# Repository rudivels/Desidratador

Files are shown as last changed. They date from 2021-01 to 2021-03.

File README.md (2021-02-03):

# Desidratador automático de laboratório 

Projeto de desenvolver um desidratador de laboratorio a partir de um forno elétrico.

Desenvolvido por [Rudi van Els](http://fga.unb.br/rudi.van) inicio dezembro 2020.
 
`/Arduino/ESP12_Secador`

`/Arduino?ESP12_Secador/ESP12_Secador_modbus`

# 1. Apresentação 

Por que fazer este desidratador?
A demanda surgiu depois de observar o trabalho demorada de levantar curva de secagem de produtos em laboratório onde era necessária  fazer medidas da perda de massa durante horas ou dias. 

Um processo típico pode levar algumas horas, com a necessidade de registrar essa perda a intervalos regulares que variam de um a alguns dezenas de minutos. 

Como não tem desidratadores que fazem essas medidas automáticas, resolvi fazer um. Em vez de pegar um desidratador pronto, resolvemos adaptar um forne elétrico, pois os desidratadores comerciais no mercado não são muito apropriados para uso no laboratório por causa do seu tamanho. 

A escolha do usar um forne elétrico é por causa da grande variedades de modelos disponíveis no mercado a preços competitos. Entretanto, nada impede de pegar a tecnologia desenvolvido e adapta-lo a um desidratador comercial.  

Foi escolhido usar um modelo de forno de 36 litros mostrada na figura a seguir.
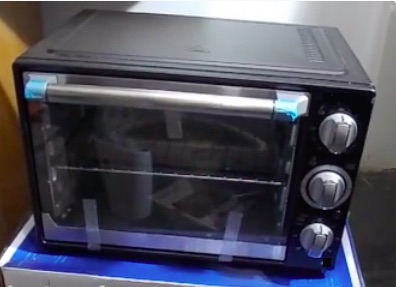
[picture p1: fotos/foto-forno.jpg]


O desidratador de laboratório deve ser capaz de:
 
- Medir a massa da amostra em tempo real durante o processo de desidratação;
- Medir dados de temperatura e umidade relativo do ar no ambiente e no desidratador;
- Armazenar estes dados no próprio equipamento;
- Controlar a temperatura dentro do desidratador;
- Controlar a vazão da entrada de ar no desidratador;
- Permitir o acesso aos dados por meio da internet;

A figura a seguir mostra a proposta do diagrama de bloco do desidratador. 

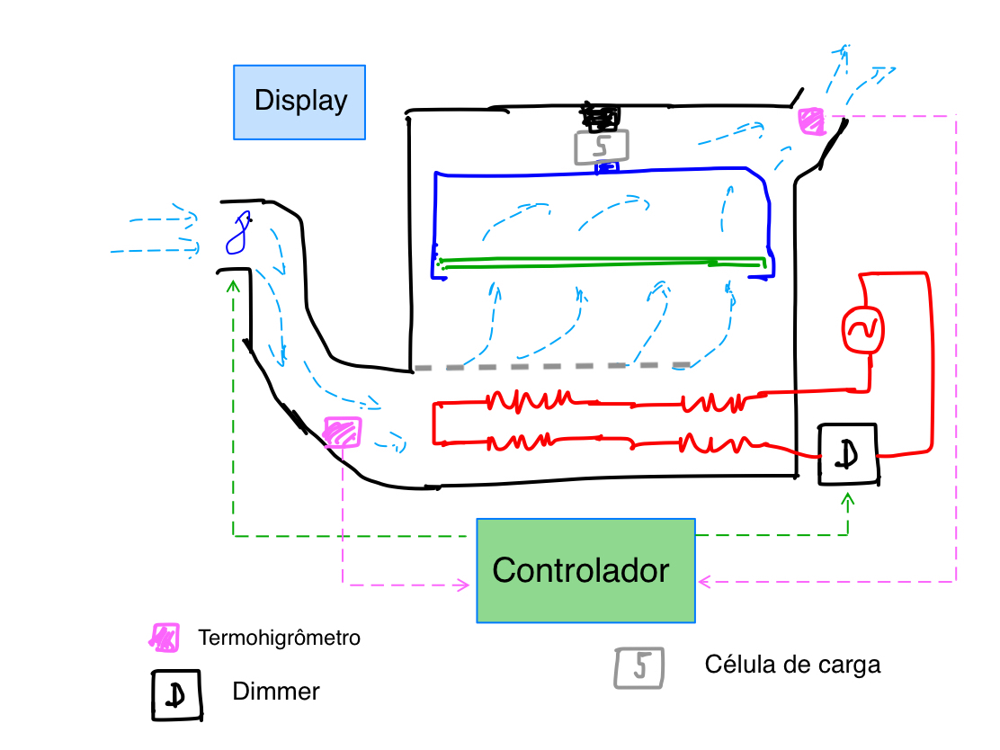
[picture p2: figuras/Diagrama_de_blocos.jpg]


O desidratador tem uma entrada de ar controlador por um ventilador, uma câmara de aqueciemento com resistores de aquecimento, uma bandeja pendurada numa balança com a amostra a ser desidratada, e uma saída de ar na parte superior. 
O equipamento mede a umidade e temperatura na entrada e saída por meio de uma unidade de controle e mostra os dados num display. 

Num futuro pretende-se desenvolver um equipamento que possa-se automáticamente fazer a desidratação a partir de uma taxa de secagem  escolhida.

# 2. Preparação

Este video mostra o forno e a proposta de transformar o forno num desidratador. [link para o video no youtube](https://www.youtube.com/watch?v=agu5u9XPCK0)

# 3. Implementação

## 3.1. Adaptação mecânica da parte interna do forno

O princípio de funcionamento do desidratador e circular ar na amostra capaz de absorver a umidade.
Para isso o ar do fora do desidratar é aquecida numa câmara de aquecimento para depois circular no desidratador e em seguida extraída para fora.
Assim vamos ter que construir uma entrada de ar controlada no lateral do forno e uma saída, tipo chamine na parte superior do forno.
A entrada de ar deve dar acesso a uma câmara de aquecimento.

## 3.2. Câmara de aquecimento 

O forno já tem resistências de aquecimento que podem ser aproveitados. Ao total o forno tem 4 resistores de aquecimento que formam dois circuitos separados com 2 resistores em serie. Cada uma das resistência tem 30 ohms. Assim a potência minima com dois resistores em série (60 ohms) ligado a rede de 220 volts é de 800 Watts.
Com os dois circuitos em paralelo o sistema pode produzir 1600 Watts.
 
Como ainda não se sabe qual a potência necessária para fazer a desidratação vamos começar fazer uma configuração com os quatro resistores em serie, colocando assim inicialmente 400 Watts de capacidade máxima de aquecimento. 

A configuração original do forno tinha um banco de resistores na parte de cima do forno e um banco com dois resistores em baixa. 
A primeira adaptação foi colocar os dois resistores da parte superior na parte de baixo do forno e abrir uma entrada para o ar no lateral, como mostrado na foto a seguir.

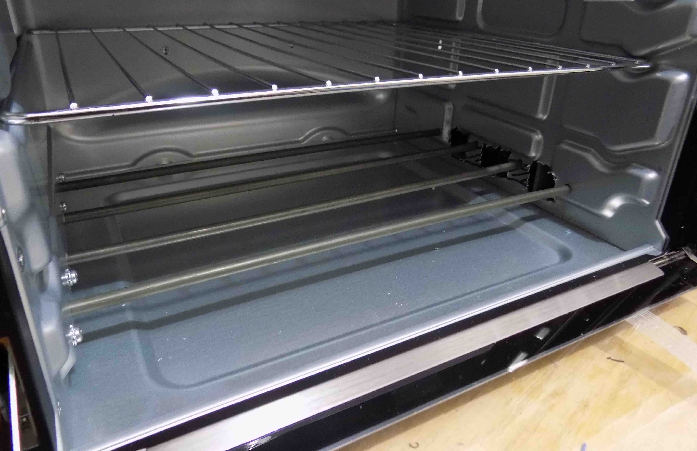
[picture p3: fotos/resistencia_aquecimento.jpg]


Para que o ar seja aquecido de forma uniformente ao no ambiente interno do forno, é necessário construir uma câmara  de aquecimento. 

### 3.2.1 Construção da câmara

## 3.3. Duto de ar de entrada
No lataral do forno foi feita uma adaptação colocando um duto de ar para captar o ar de fora por meio de um ventilador que pode ter sua velocidade controlada.

O video mostra a adaptação e o duto de ar. 
[Video com a apresentação do duto de ar de entrada ](https://www.youtube.com/watch?v=D7OGNmsQnvQ)

A foto a seguir mostra a entrada de ar no lateral do forno, com os 4 resistores de aquecimento lado ao lado.

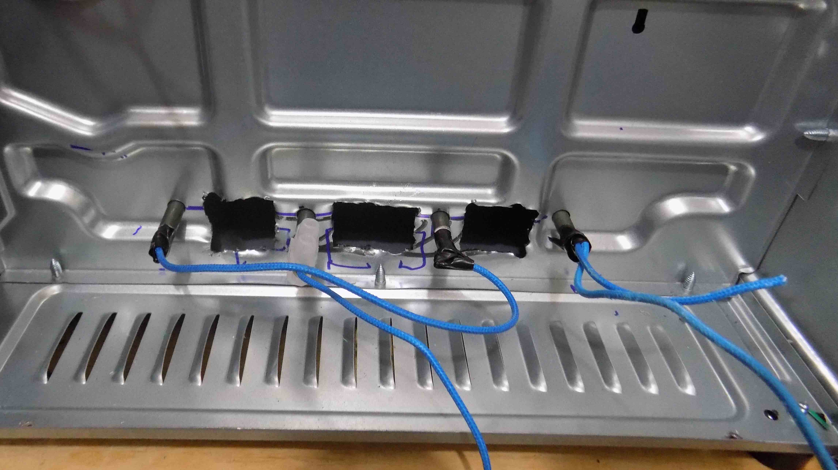
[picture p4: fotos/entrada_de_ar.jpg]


O duto de ar impresso com impressora 3D foi construido para servir de suporte para a FANe levar o ar externo para dentro do forno. 
A figura a seguir mostra a monagem do conjunto.

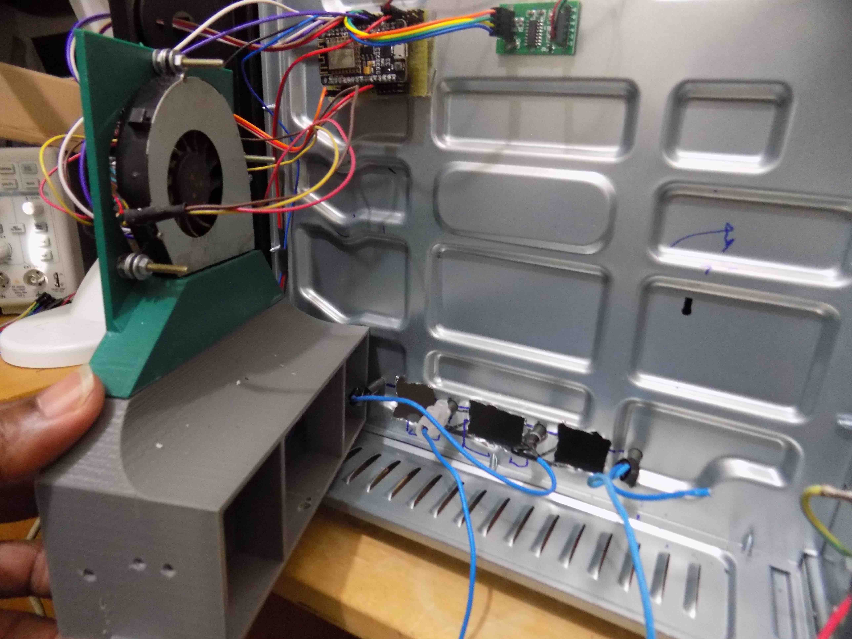
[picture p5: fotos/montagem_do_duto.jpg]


Um vez montada o sistema fica como mostrado na próxima foto.

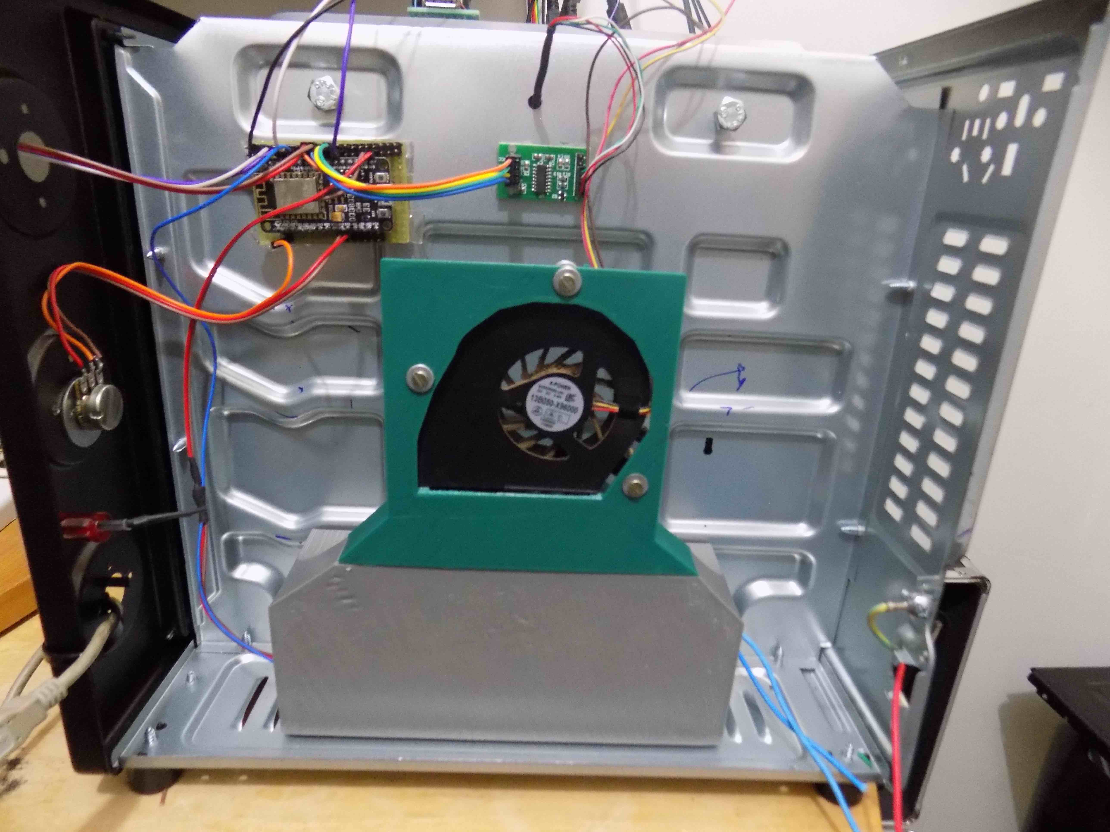
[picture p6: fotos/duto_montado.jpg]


### 3.3.1. Medição de umidade e temperatura no duto de entrada

A foto mostra o medidor de umidade e temperatura DHT11 instalada no duto de entrada do ar.

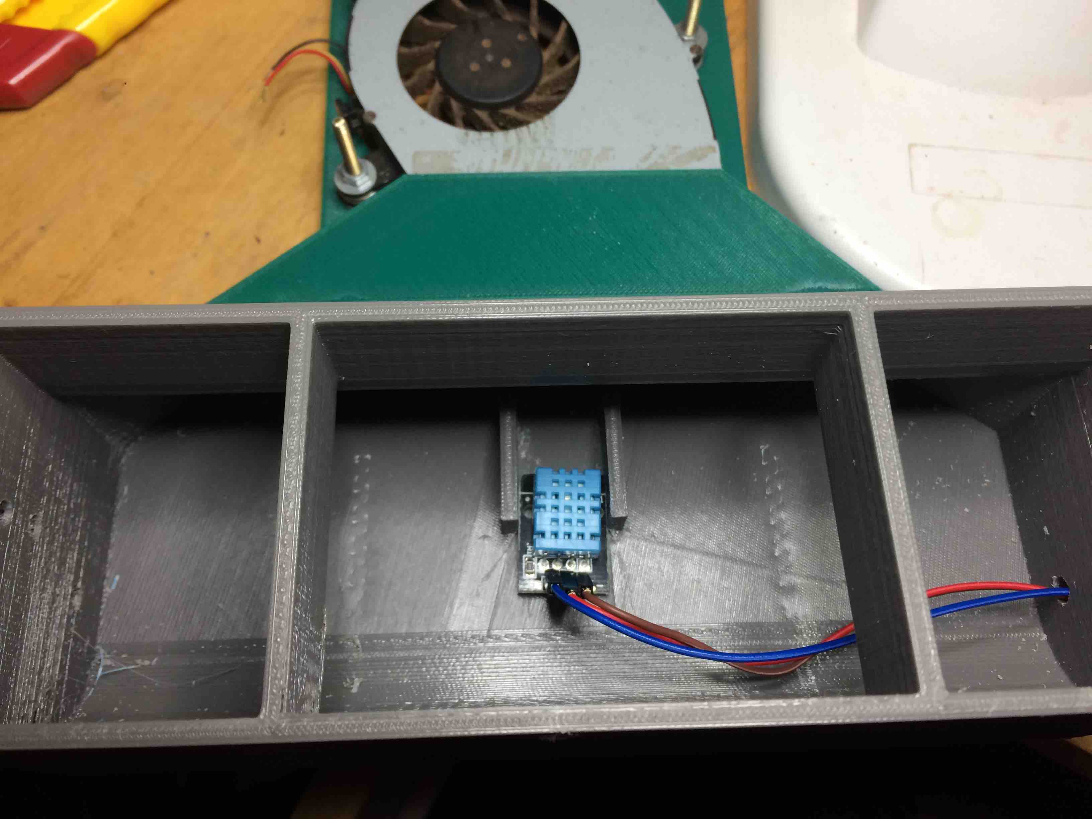
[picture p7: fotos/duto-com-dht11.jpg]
 

## 3.4. Balança eletrônica

Uma das principais necessidades do desidratador é de poder medir a massa da amostra sem ter que tira-lo do equipamento. 
Para fazer isso foi construído na parte superior do forno um suporte para fixar uma balança eletrônica que por sua vez permite pendurar uma bandeja. 
A estrutura de suporte da bandeja foi construido em aluminio e tem, junto com a bandeja uma massa de aproximadamente xxx gramas.
A foto a seguir mostra o suporte e a bandeja. 

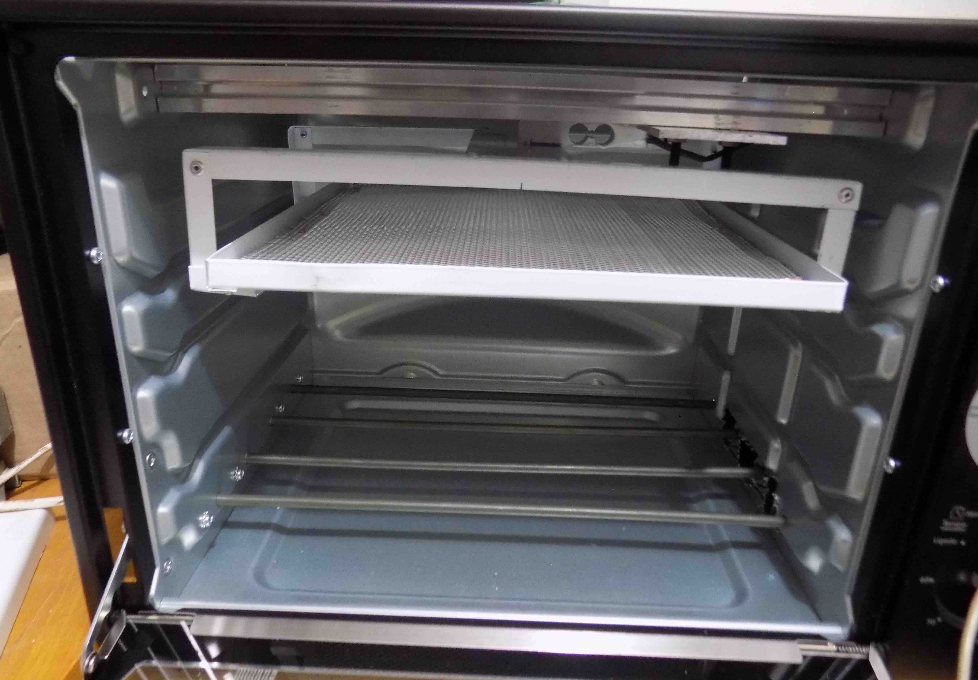
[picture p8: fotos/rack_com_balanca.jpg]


A balança eletrônica tem como elemento central uma célula de carga com capacidade de medir até 1 kg.
Dessa forma pode se colocar amostras de até 500 gramas, que bastante suficiente para uma amostra de secagem. 

A foto em baixo mostra o detalhe da instalação da célula de carga. 

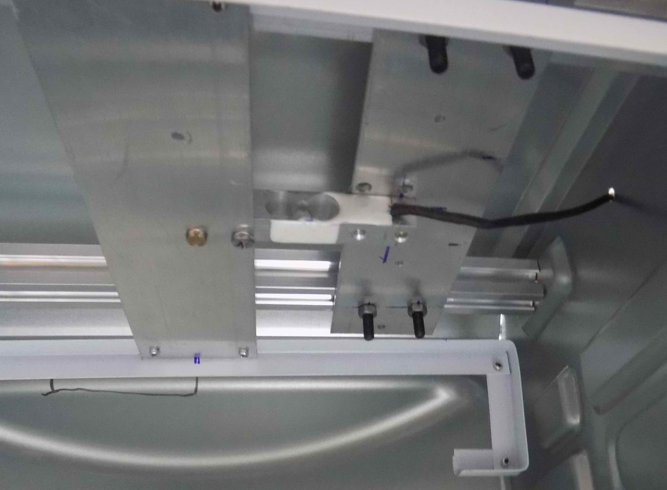
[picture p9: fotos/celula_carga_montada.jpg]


A estrutura montada para suportar a celula de carga e a bandeja a ser pesado é mostrado nas fotografias a seguir.

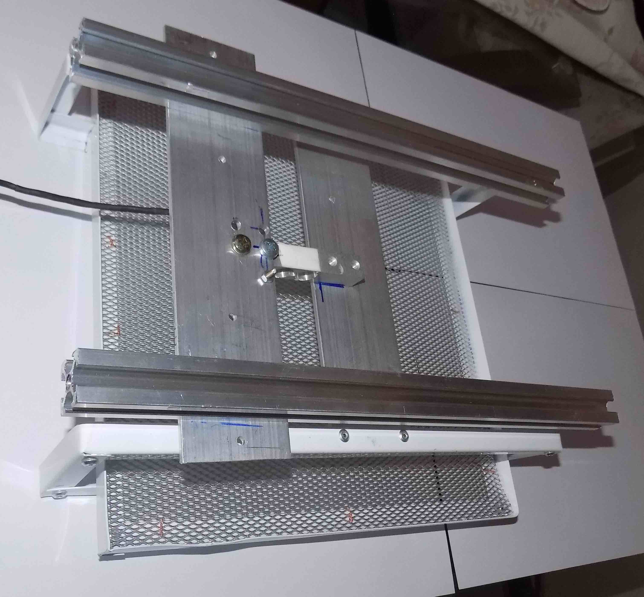
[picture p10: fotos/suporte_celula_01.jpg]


Detailhe do suporte.

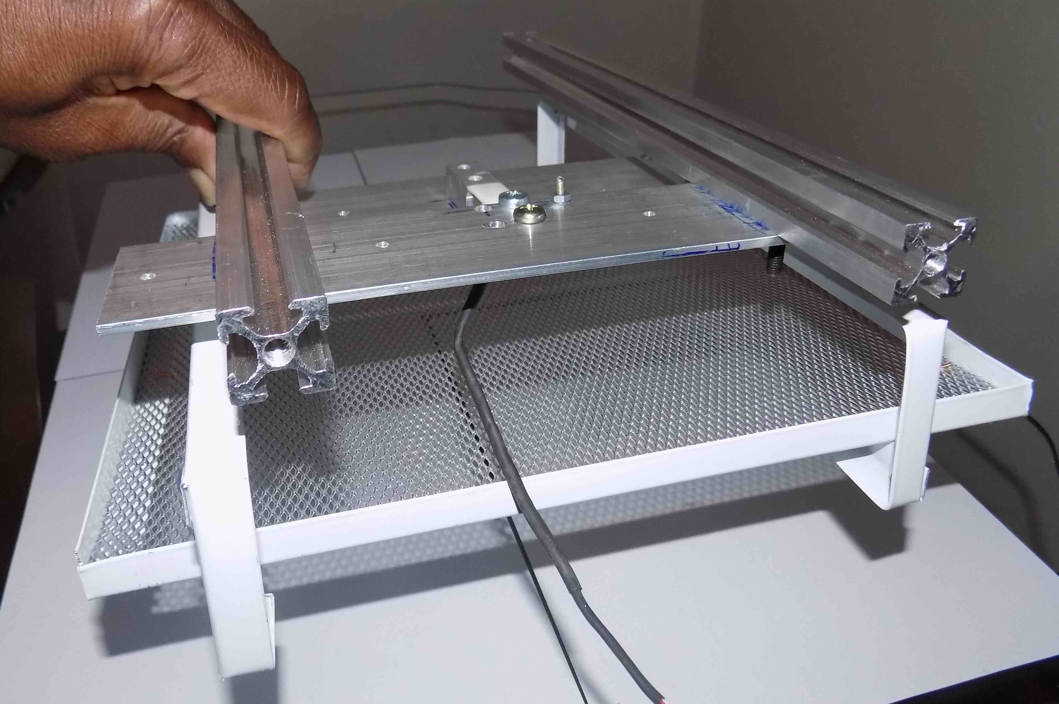
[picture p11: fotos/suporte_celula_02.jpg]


O video a seguir mostra a balança instalada e funcionando no forno fazendo a pesagem automática. 

[Video com o protótipo da pesagem automática](https://www.youtube.com/watch?v=mP0JLjlJqJM)

A célula de carga é ligado a um amplificador de instrumentação HX711 que é processado pelo microcontrolador que comando todo funcionamento do sistema. 

## 3.5. Fonte de alimentação

Foi instalada uma fonte de alimentação para alimentar os novos componentes eletrônicos e o microcontrolador. A fonte fornece o 5 volts cc para a alimentação do microcontrolador e 3.3 Vcc para os demais componentes eletrônicos.
A foto a seguir mostra a fonte instalada no desidratador. 

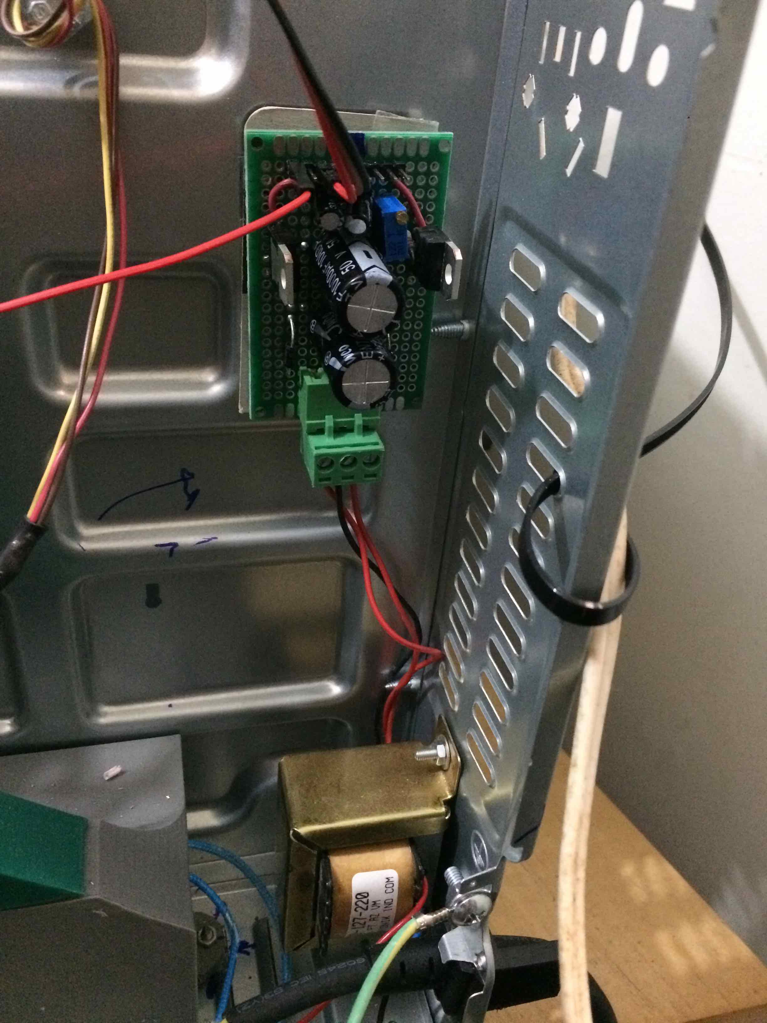
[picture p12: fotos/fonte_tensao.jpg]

Entrada 220Vac
Sáida - 5Vcc @ 1 amp. e 3.3 Vcc @ 1 amp.

# 4. Controle

O circuito de controle tem que ser capaz de medir os variáveis do processo de secagem e ajustar os paramatros do processo.

Os seguintes dados serão registrados de forma automática durante o processo de secagem num intervalo de tempo que pode ser programado:

- Temperatura ambiente 
- Umidade relativa do ar no ambiente
- Temperatura no desidratador
- Temperatura na saída do ar do desidratador
- Umidade relativa na saída de ar do desidratador
- Peso do material no desidratador

Estes dados serão armazenar no próprio secador e vai ser possível accessar estes dados diretamento pela internet em tempo real.

O desidratar vai permitir controlar os seguintes parâmetros do processo de secagem:

- potência aplicado no resistência de aquecimento
- Velocidade do ventilador de entrada do ar

Estes controles devem ser disponibilizados não somente localmente nos botões de operação do desidratodor, mais também por meio de  comandos via internet.

O elementos central do controlador é o microcontrolador ESP12F
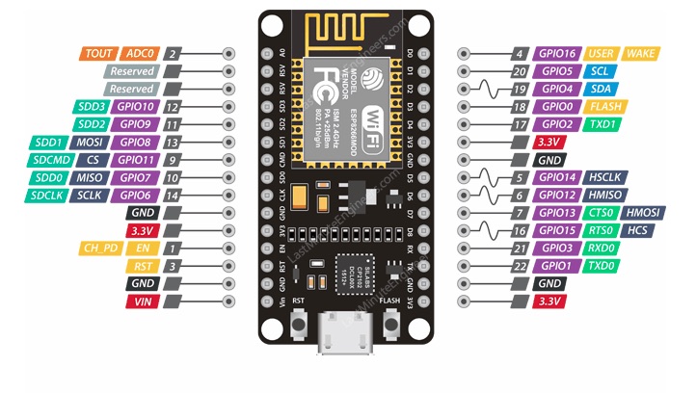
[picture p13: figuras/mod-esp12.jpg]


| Modulos | Descrição |
|:--------|:----------|
| DHT11   | Temperatura e umidade da entrada do ar |
| DHT11   | Temperatura e umidade da saída do ar |
| HX711   | Peso |
| DS18B20 | Temperatura na célula de carga e na câmara|
| Dimmer  | Regular potência de aquecimento |
| FAN     | Ventilador de regula entrad de ar |
| Fonte   | Alimentação de 5v e 3.3v

A interligação do ESP12F com os diversos componentes é mostrada na figura a seguir

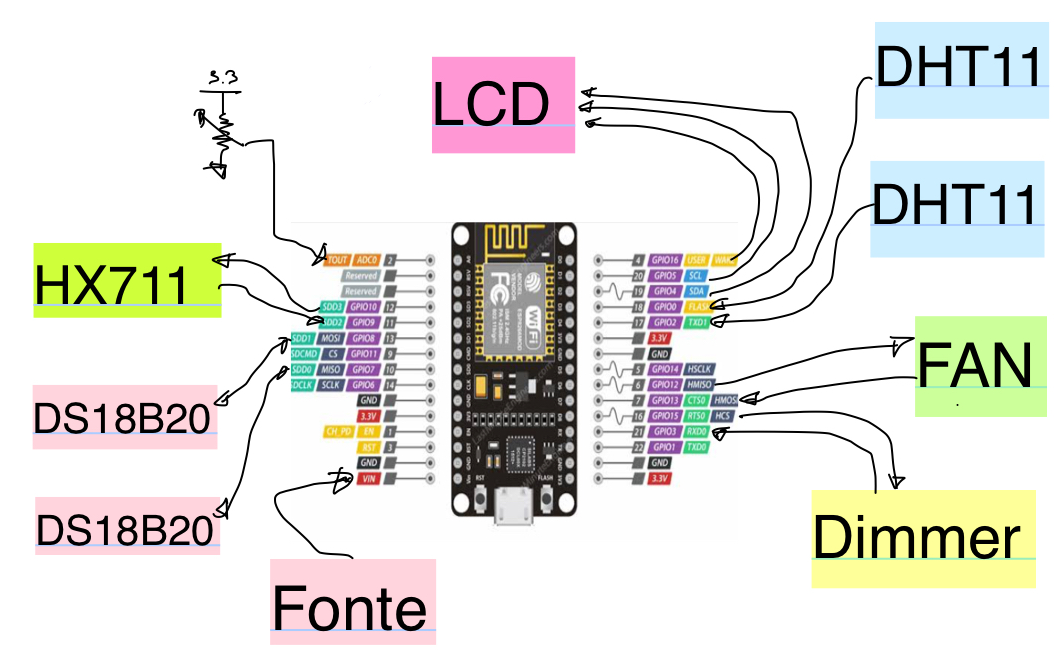
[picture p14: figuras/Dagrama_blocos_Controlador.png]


Devido as limitações do ESP12 teve que se tirar o LCD e um dos DS18B20, pois nem todos os pinos do ESP podem ser usados como pinos de entrada e saída. 

Os pinos para ligar os módulos sao documentados na tabela a seguir.

| porta | GPIO   |função         | 
|------:|:-------|---------------|
|  D0   | GPIO16 | Chave para habiltar calibração |              
|  D1   | GPIO5  | DS18B20       |
|  D2   | GPIO4  | FAN PWM       |
|  D3   | GPIO0  | DHT 11        |
|  D4   | GPIO2  | DHT 22        |
|  D5   | GPIO14 | HX711 DOUT    |
|  D6   | GPIO12 | HX711 SCK     |
|  D7   | GPIO13 | FAN Rotacao   |
|  D8   | GPIO15 | RES PWM       |
|  A0   |        | potenciômetro |  

Uma proposta de macro esquema elétrico é mostrado no diagrama elétrico a seguir 

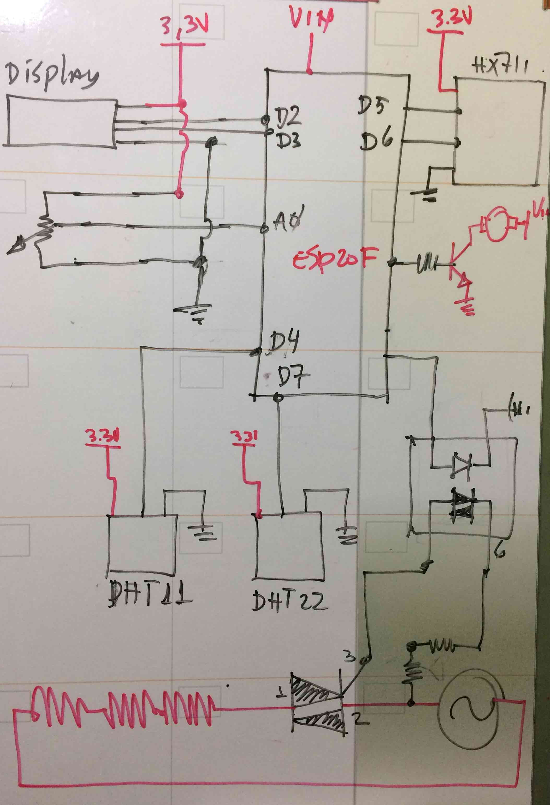
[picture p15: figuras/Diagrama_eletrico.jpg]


## 4.1. Circuito de acionamento da FAN

O circuito de acionamento do ventilador é mostrada a seguir.
O ventilador tem um circuito de realimentação que mede a rotação e disponibilize este dado por meio de um circuito coletar aberto.
  
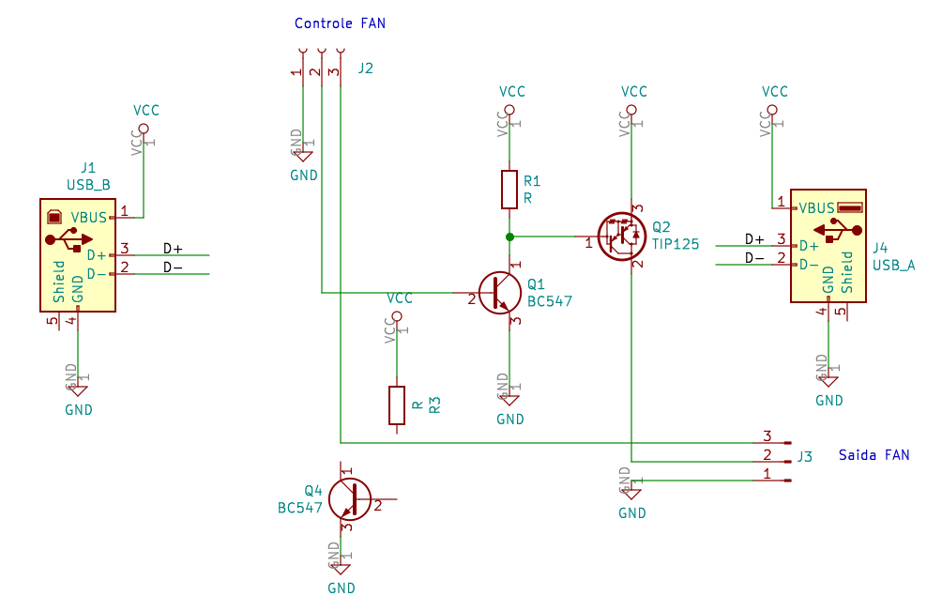
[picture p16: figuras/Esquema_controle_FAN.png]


A foto a seguir mostra a implementação do acionador *driver* de potência do ventilador e as portas USB para sua alimentação. 
 
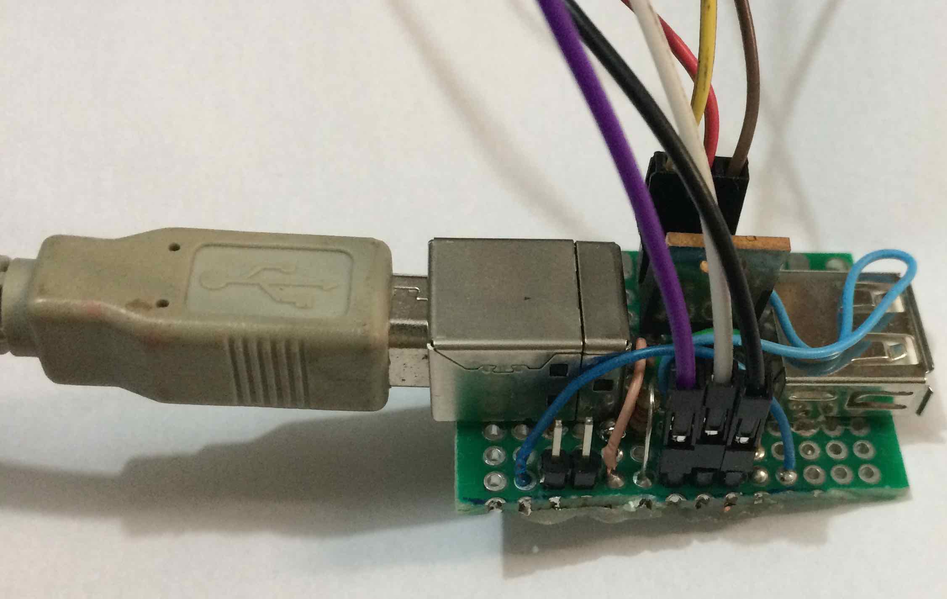
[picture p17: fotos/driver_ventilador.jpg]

O sinal de velocidade foi medido no osciloscópio e chega até 100hz quando alimentado com 5 volts. 
Pretende se variar o acionamento por meio de um sinal PWM gerado pelo microcontrolador. 
O PWM do ESP-12F tem uma frequencia de 1kHz e um range de [0-1024] que já vem configurado ao chamar a função `analogWrite(pino , valor);` do Arduino IDE. 

Percebe-se que o ventilador tem uma zona morta que fica em torno de 600 unidades do PWW ou seja 600/1024 * 4,8 volts.

Com controle manual em malha aberta mostra que é possivel com um pouco de sensibilidade ajustar a velocidade até mais ou menos 50Hz.
Valores a baixo disso são difícis de ajustar manualmente em malha aberta.

Isso pode ser um problema, quando queremos ajustar uma vazão de ar de entrada nessa faixa no desidratador.  

Para poder controlador a velocidade da FAN mais precisa e obter baixas vazões de entrada de ar estável no desidratador, vai ser necessária fazer um algoritmo de controle com o usando o sinal de velocidade com realimentação. 

O sinal de velocidade da FAN foi ligado a entrada de interrupção externa no pino D7 do microcontrolador ESP-12F para poder medir a frequencia gerado pela FAN a cada segunda.

Uma tentativa de implementar o controle proporcional simples, tendo como taxa de amostragem 1 segundo com valores de ganho do controlador de variando entre 6 e 15 não deu um resultado muito satisfatório e o sistema ficou instável. 

Isso mostra que vai ser necessário sintonizar um controlador PID. 
O primeiro passo foi fazer um ensaio ao degrau medindo o tempo entre cada interrupção gerado pelo sensor de velocidade da FAN e armazenando o tempo numa vetor de 200 pontos.  

O programa no Arduino que armazena os dados medidos e mandar para o Octave e mostado a seguir.

```
void ICACHE_RAM_ATTR handleInterrupt() 
{
 interruptCounter++;
 if (start==1)
 {
  temp_millis_ant=temp_millis;  
  temp_millis=millis();
  delta_millis=int(temp_millis-temp_millis_ant);
  medidas[i]=delta_millis;
  i++;
  if (i>=tam) start=0;
  }
}

void setup() 
{
 pinMode(PWM_FAN, OUTPUT);
 pinMode(SENS_ROT, INPUT_PULLUP);
 pinMode(D8, OUTPUT);
 digitalWrite(PWM_FAN, 0); 
 Serial.begin(115200);
 delay(1000);
 attachInterrupt(digitalPinToInterrupt(SENS_ROT), handleInterrupt, FALLING);
 Serial.println("Pronto  ");
}

unsigned long previousMillis = 0;
int ledState = LOW;
int erro =0;
int saida =0;
int inByte;

void loop() 
{
 digitalWrite(PWM_FAN, 0); 
 Serial.flush();
 delay(1000);
 while (Serial.available()==0);
 inByte = Serial.read();
 temp_millis=millis();
 start=1;
 digitalWrite(PWM_FAN, 1); 
 i=0;
 delay(5000);
 for (i=0;i<tam;i++)
 {
  Serial.println(medidas[i]);
 }
 Serial.flush(); 
 delay(1000); 
} 
```

O programa em Octave que leu, tratou e plotar essas medidas do Arduino de forma automática está listado a seguir.

```
# Programa /Users/rudi/src/octave/secador/testa1.m
# o programa espera os dados do Arduino com os 
# 200 primeiras interrupcoes e os respectivos tempos em cada 
# interrupçao para plotar o grafico

pkg load instrument-control

s1 = serial("/dev/tty.SLAB_USBtoUART");
pause(1);
srl_flush(s1);
srl_write(s1,"1");
data=char(srl_read(s1,260));  # 200
cc=textscan(data,"%f");
fclose(s1);
lin=transpose(cc{:}) * 0.001;  # valores em millisegundos
tam=length(lin);
t=[1:tam];
x=lin;
vel=lin;
x(1)=lin(1);
for i=1:(tam-1)  x(i+1)=x(i)+lin(i+1); endfor
for i=1:(tam)    vel(i)=1/lin(i);      endfor 
plot(x,vel,x,vel,"*")
title("Resposta ao degrau");
xlabel("tempo em segundos");
ylabel("frequencia em Hz");
```

O resultado desse ensaio é mostrada na figura a seguir, 

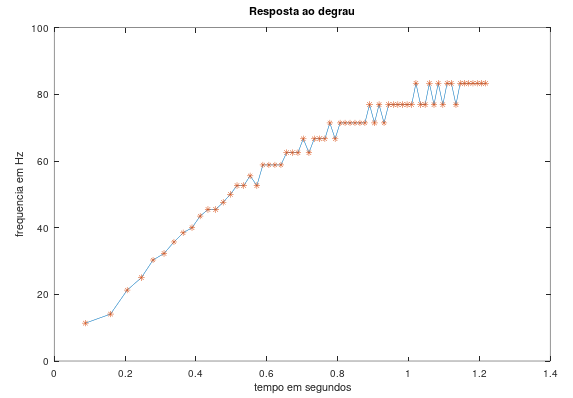
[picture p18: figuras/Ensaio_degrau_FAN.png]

Eixo x = Tempo em milisegundos ; 
Eixo y = Frequencia.

A proposta agora é projetar um controlador para poder garantir uma velocidade e consequentemente uma vazão controlada no desidratador. 

O desafio vai ser montar uma estratégia de controle pendurada na interupção do próprio sensor e usar como referência o tempo entre cada interupção, ou sintonizar um controlador PID com taxa de amostragem de 1 segundo capaz de garantir o controle. 

Analisando a constante de tempo de 400 ms do ventilador, surge a pergunta. É possivel calcular um controlador digital proporcional capaz de ter uma resposta estável para um sistema de primeia ordem do tipo 1 com taxa de amostragem de 1 segundo ?

Será que pode ser mostrado teoricamente que para estes casos se precisa de um controlador que lembro das amostras anteriores, como por exemplo PI e PD?

Como o foco deste texto não entrar na teoria de controle, vamos disponibilizar um outro repositório para explicar essa questão, mostrando o passo a passo da sintonia, usando o hardware disponível e as ferramentas de análise e sintonia de controladores do Octave.
O resultado dessa pesquisa será incorporado no controle de velociade do desidratador.  

## 4.2. Circuito de acionamento da resistência de aquecimento

Outra parte crucial no desidratador é a capacidade de controlar a temperatura na camara de aquecimento e consequentemente a temperatura do ar que entre no desidratador.

Para isso vai ser necessária controlar a potência dissipada nos resistores de aquecimento usando o princípio de um Dimmer. Só que neste caso o Dimmer será diretamente controlado pelo microcontrolador a partir da leitura das variáveis de temperatura, humidade do ar e velocidade do ar de entrada.

O circuito que permite o acionamento das resistências de aquecimento é mostrado a seguir.  

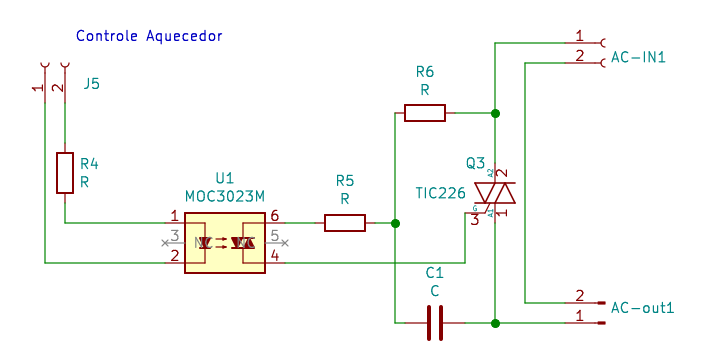
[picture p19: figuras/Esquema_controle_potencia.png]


Datasheet do triac.

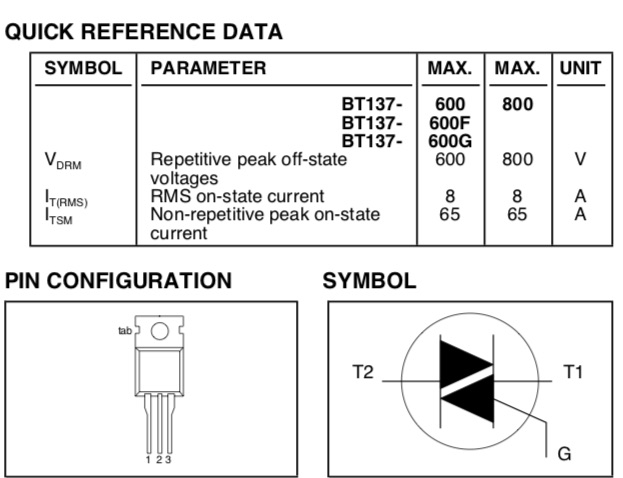
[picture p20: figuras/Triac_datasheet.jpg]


É um circuito clássico de chave eletrônico por meio de um Triac (BT137 ou TIC226) acionado por um opto acoplador de isolamento MOC3023. O diode emissor de luz (led) dentro do MOC3023 é que aciona o circuito de potência. A vantagem dessa abordagem é que pode-se ligar diretamente o led à uma porta do microcontrolador e usar a mesma estratégia de variar a potência por meio da técnica PWM usado para acionar o circuito de velocidade. 

Entretanto, como a resistência é acionado por uma fonte de potência AC da rede elétrica comercial que tem uma frequencia de 60Hz, vamos implementar a frequencia de chaveamento do PWM a uma frequencia muito mais lento que frequencia da rede elétrica. Isso é divido a própria característica do Triac e também pela limitação de tempo de chaveamento do led. 

Como se trata de um processo térmico onde a constante de tempo é muito lento, na ordem de dezenas de segundos, podemos escolher qualquer frequencia pelo menos dez vezes menor que a frequencia da rede. 

Se o aquecimento fosse feito com lâmpadas incandescente, seria intessante usar uma outrá técnica de acionamento que evitasse a efeito visual da variação da luz. Neste caso poderia se optar por circuitos de acionamento mais sofisticado que modulam a largura do pulso da própria tensão da rede. 

Como nosso circuito é resistivo, podemos usar essa estratégia mais simples. Outra questão que tem que depois ser avaliado é a interferência que o circuito de chaveamento de potência pode causar nos circuitos de medição de temperatura, humidade, célula de carga e a velocidade da FAN. 

Mas isto será avaliada experimentalmente. 

A foto mostra o circuito montado.

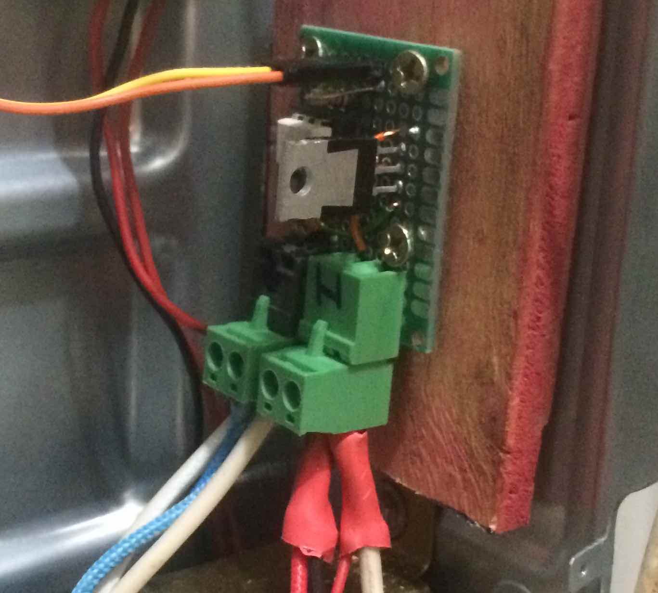
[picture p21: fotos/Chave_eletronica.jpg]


O circcuito foi testado e a frequencia de chaveamento que melhor funcionou foi de 6 Hz. 
A única inconveniente é que em todas as frequencias testadas a lampada incandescente piloto fica piscando.
Para resolver isso deveria-se sincronizar a modulação de largura de pulos com a frequencia da rede elétrica, mas isso leva a uma carga excessiva de programação. 

O jeito simples é retirar a lampada piloto.

## 4.3. Algoritmo de controle de temperatura

Para implementar o algoritmode controle de controle de temperatura precisamos identificar o modelo dinâmica do sistemas.

O primeiro passo é fazer um enasio a uma entrada degrau e medir o comportamento da temperatura. 

O ensaio será realizado nas condições normais de operação do desidratador, com o ventilador ligada em 600 de 1023 unidades, a potencia da resistência também ligada em 600 
de 1023 unidades, e a saída de ar aberta.

Ao ligar o desidratador nessas condições em malha aberta colocando a potencia da resistência de aquecimento em 600 de 1023 unidades, a temperatura no forno chegou a 80 graus celcius em aproximadamente 20 minutos e continua aumentando. 
O relatório do ScadaBR mostra a seguinte figura.

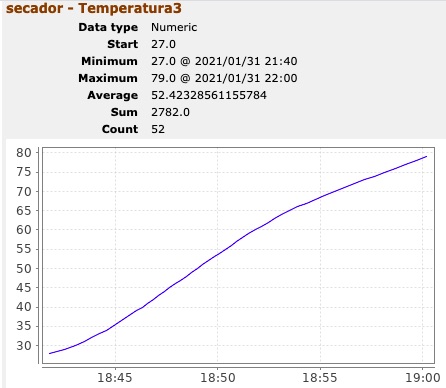
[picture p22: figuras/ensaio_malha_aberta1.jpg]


Como a temperatura chegou além do ponto de operação do desidratador, vamos mudar o ensaio e colocar um degrau de malha aberta de 300 de 1023 unidades.

Além disso, vamos colocar um peso inerte de 321 gramas para também avaliar o comportamento da célula de carga em função da temperatura.

### 4.3.1. Ensaio a degrau

O ScadaBR que monitora os dados do desidratador gera um relatorio com os valores de todos os sensores com seu respectivo o horário. 
O trecho a seguir mostra o formato de gravação desses dados do ScadaBR.

```
secador - Temperatura3,2021/01/31 22:52:27,28.0,28.0
secador - Temperatura3,2021/01/31 22:53:39,29.0,29.0
secador - Temperatura3,2021/01/31 22:54:37,30.0,30.0
secador - Temperatura3,2021/01/31 22:55:15,31.0,31.0

```
Este arquivo é gravada no formato CSV e pode ser acessado por um programa em Octave. 

```
# Programa /Users/rudi/Desktop/ensaio_controle_temp/ensaio1.m
# o programa espera os dados do relatorios do ScadaBR para plotar o grafico
# entrada degrau 300/1023 unidades  saida graus

pkg load io
X = csv2cell('temp.csv',',');
#
#  [1,1] = secador - Temperatura3
#  [1,2] = 2021/01/31 22:50:39
#  [1,3] =  28

X(:,2);
t=datenum(X(:,2),"yyyy/mm/dd HH:MM:SS");
tempo=t;
temperatura=t;
tempo(1)=0;
for i=2:length(t)
    tempo(i)=(t(i)-t(1))*24*60*60;
endfor    

tp=X(:,3);
for i=1:length(t)
   temperatura(i)=tp{i,1};
endfor

plot(tempo,temperatura,tempo,temperatura,'*');
grid
title("Resposta ao degrau Entrada 300/1023 PWM");
xlabel("tempo em segundos");
ylabel("temperatura em graus");
```

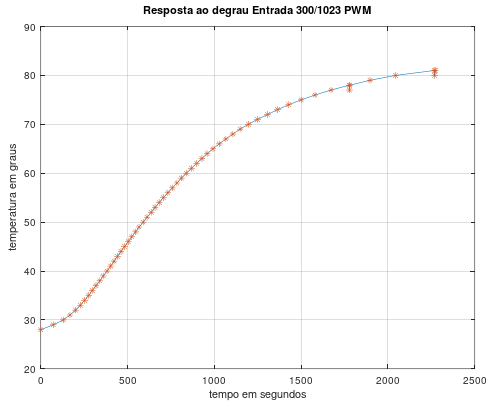
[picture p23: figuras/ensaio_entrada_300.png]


Com este ensaio é possível parametrizar o modelo. 

### 4.3.2 Modelo de sistema de primeira ordem

Y(s) / U(s) = K / ( t s +1) 

onde K é o ganho e t o constante de tempo.
Considerando o valor final da curva de temperatura em 85 graus para um degrau de 300 de 1023 unidades.

O ganho noss caso será  K = ( 85 - 27 )/ 300

O constante de tempo t é o tempo que a curva atinge 63% do valor final. 
Ou seja 62,3% do valor final é 53 graus celcius e este valor é atingido no instante de 658 segundos. 

Y(s) / U(s) = 0,1933 / (658 s +1 )

```
# Simulacao do modelo tomando como valor inicial 27 graus celcius
# e uma entrada degrau de 300 unidades
num = (85-27)/300;
den = [658 1];
t=(0 :1 :2500);
sys = tf (num , den);
[y , t, x ]=step(sys, t);
plot(t,y*300+27)

```
A figura mostra o modelo simulado e a resposta real.
Dá para ver claramente a necessidade de incorporar o atraso de tempo do sistema.

Entretanto creio que com um controlador PI será possível regular a temperatura.  

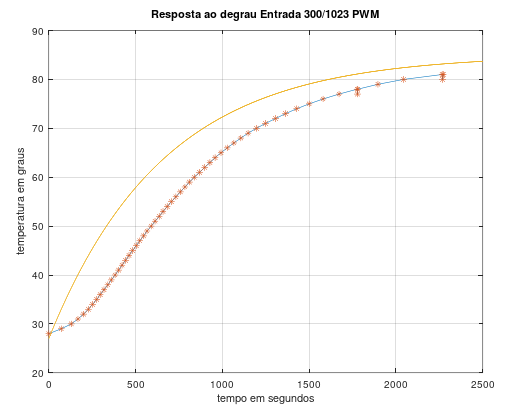
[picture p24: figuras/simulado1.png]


### 4.3.3 Controlador PID 

D(s) = Kp ( 1 + 1 / Ti s + Td s )

Vamos usar o método clássico de sintonia do controlador de PID, método de resposta ao degrau ou primeiro método de Ziegler Nichols.
O método usa o atraso de tempo "L" e a constante de tempo "T" e a taxa de reação que é R = A / T

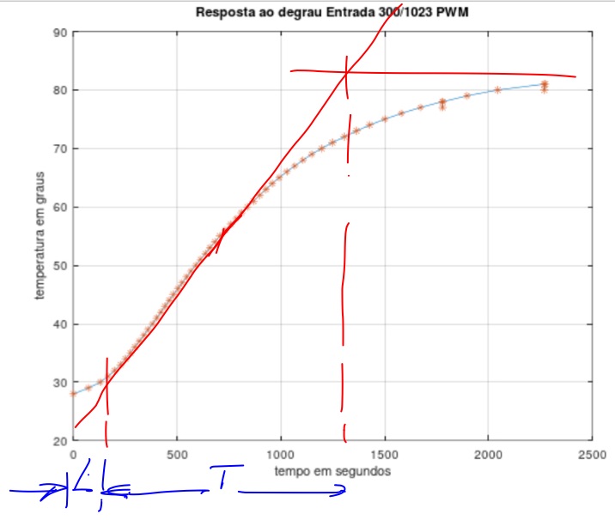
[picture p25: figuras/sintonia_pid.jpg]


L = 150 e  T = 1200 segundos e R = A /T  = (85-27)/1200 = 0,048;   RL = 0,048 * 150 = 7,25
1/ RL = 0,138

| Tipo | Kp       |  Ti     | Td    | 
|-----:|:--------:|:-------:|:-----:|
| P    |   1 / RL | inf     | 0     |
| PI   | 0,9 / RL | L / 0,3 | 0     |
| PID  | 1,2 / RL | 2 L     | 0,5 L |

| Tipo | Kp    | Ti  | Td | 
|-----:|:-----:|:---:|:--:|
| P    | 0,138 | inf | 0  |
| PI   | 0,124 | 500 | 0  |
| PID  | 0,166 | 300 | 75 |

Simulação do controlador e do processo.

```
num = (85-27)/300;
den = [658 1];
t=(0 :1 :2500);
sys = tf (num , den);
#[y , t, x ]=step(sys, t);
#plot(t,y*300+27)

# controlador PID
contr = pid(9.6, 300, 75);
# Sistema em malha aberta
sist_abert = blkdiag(sys, contr);
# Sistema em malha fechada
sist_fech  = feedback(sist_abert);
# Simulação da entrada a degrau
step(sist_fech,t);
#plot(t,y*300+27)

```

### 4.3.4  Implementação do controlador  digital

O controlador proportional integral derivativa tem a seguinte implementação:

```
U(s) / E(s) = Kp ( 1 + 1/ Ti s + Td s)
```

Para implementar o controlador pelo seu equivalente discretizado vamos utilizar o método da aproximação retangular para o integrador e o método da aproximação retangular regressiva para o controlador derivativa.
 
Para o termo integrativo substituimos  s por  (z-1)/T 

Para o termo derivativo substituimos  s por  (z-1)/ Tz  

O tempo e amostragem T  é de 1 segundo  

Resolvendo o sistema e tomanda a transformada inversa chega se ao seguinte algoritmo de controle 

```
U(t) = U(t-1) + q0 E(t) + q1 E(t-1) + q0 E(t-2)

onde q0 = Kp (1 + Td) = 0.125   =  49,96
     q1 = Kp (-1 + 1/Td - 2Td ) = -99,76
     q2 = Kp * Td               =  49,80

```

ou sua implementação no arduino fazendo U=Saida e E é sinal de erro.
Uma problema que apareceu é a saturação do termo integral *intregral windup* que foi retirado por meio de uma sentença *if else*

```
void interrupcao_1segundo(void)
{
 Saida_1 = Saida;
 Erro_2 = Erro_1;
 Erro_1 = Erro;
 Erro = Referencia - Temperatura; 
 Saida = Saida_1 + q0 * Erro +  q1 * Erro_1 + q2 * Erro_2;
 if (Saida > 1023) {analogWrite(PWM_RES,1023); Saida=1023;}
  else
   if (Saida => 0) analogWrite(PWM_RES, Saida); 
    else { analogWrite(PWM_RES, 0); Saida=0;}
}
```

O controlador PID sintonizado por este meio não funciou de acordo conforme pode ser visto nas fuguras.
O setpoint nessa condição era de 

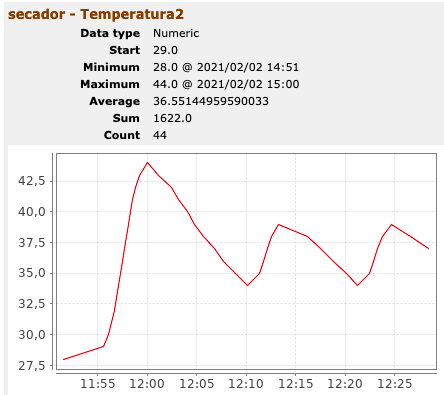
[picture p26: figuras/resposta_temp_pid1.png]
 

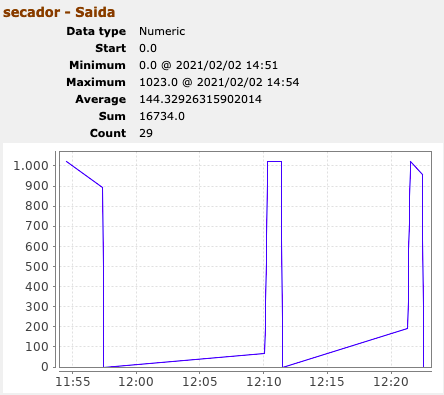
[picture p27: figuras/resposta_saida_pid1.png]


Fizemos alguns ajustes dos parametros por tentativa e erro, mas mesmo assim o sistema ficou oscilando muito. 

Vamos ter que partir para outra estratégia de controle, usando os métodos classicos de alocação de polos ou um feedforward so 

## 4.4. Algoritmo de compensação de temperatura da balança 

Um desafio deste projeto é de fazer a compensação da medição de massa com o aumento da temperatura, já que o ensaio vai ser realizado com temperatura bem a cima de temperatura ambiente para qual o sensor é calibrado.   

A especificação técnica da célula de carga o sensor deve aguantar temperaturas até 70 graus, mas deve ter uma distorção da medição com o aumento da temperatura. 

Um ensaio num outro projeto [1] com uma celulá de carga com a mesma caracterítica levantou o comportamento da mesma em relação aumento de temperatura. A figua a seguir mostra que uma amostra inerte de massa conhecido submetido a um ensaio. 

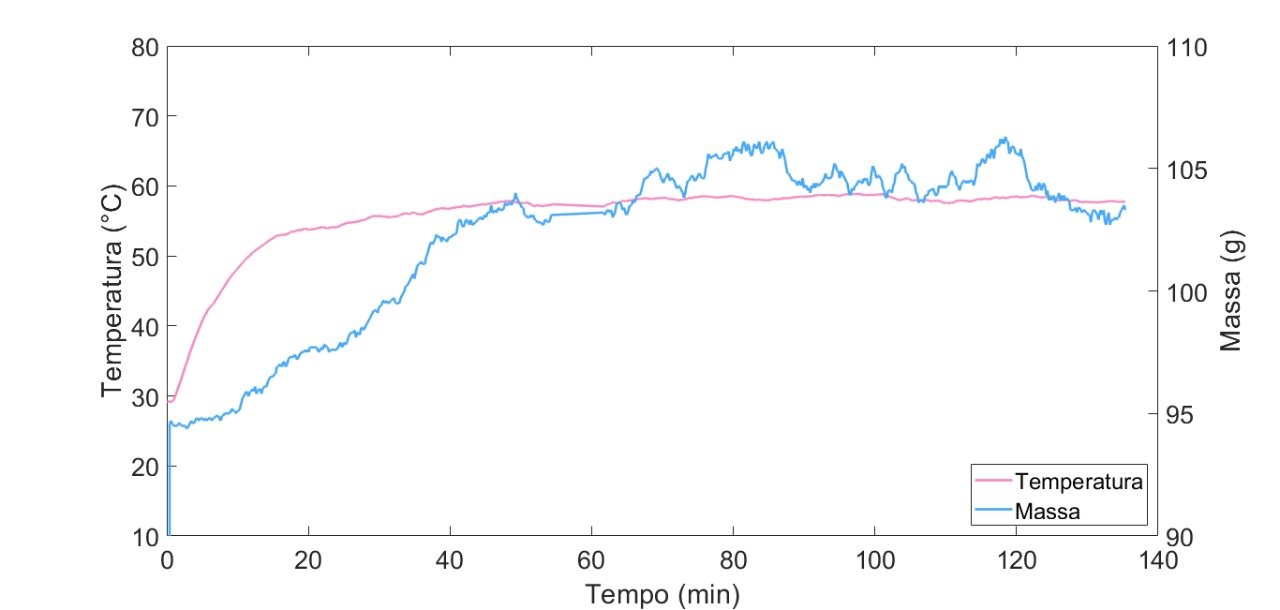
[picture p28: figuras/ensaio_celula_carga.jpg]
  

Chega se a conclusão que tem para um aumento de 30  graus celsius tem-se um aumento de aproximadamente 10 gramas no valor inicial de 95 gramas.
Isso dá um aumento de 0,35% por incremento de grau celcius.

Convem mencionar que este foi o primeiro ensaio e que são necessários mais ensaios para fazer uma calibração mais precisa.
Também é necessário modelar o retardo ou atraso do processo e avaliar sem tem algum efeito de histerese.

[1] Santos I da S, Mendonça ARV, Els RH van. Instrumentacão de secador de bandejas. Congr. iniciação científica Univ. Brasília, 2020.

### 4.4.1. Compensação dinâmica 

Para a compensação da leitura da massa com a célula de carga é necessário fazer a compensação do efeito da temperatura na célula. 
Para isso, foi colocado um sensor de temperatura colado na célula de carga conforme mostrado na figura a baixo.

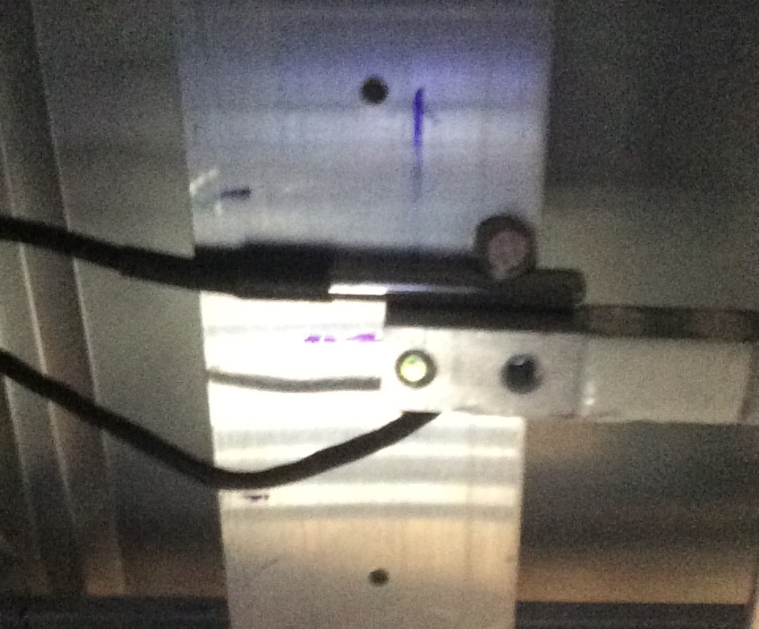
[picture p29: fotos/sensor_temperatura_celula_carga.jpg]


Também devemos estudar ainda o comportamento da temperatura no ambiente do desidratador e a temperatura nas partes metálicos da parede do forno. 
A célula de carga está fixado a uma barra de alumínio que por sua vez está ligado a parede do forno. Isso pode influenciar no comportamento térmico. 
Uma alternativa que se pode avaliar no futuro é de usar uma chapa não metálica e bom isolante térmica para fixar a célula de carga, assim isola-lo.

Também percebeu-se o atraso entre a inflencia da temperatura na deformação do metal.

Vamos aqui fazer uma série de ensaios para identificar o modelo da celula de carga em função da temperatura e fazer a compensação dinâmica da massa.   

# 5. Resultados

# 5.1. Teste com majericao

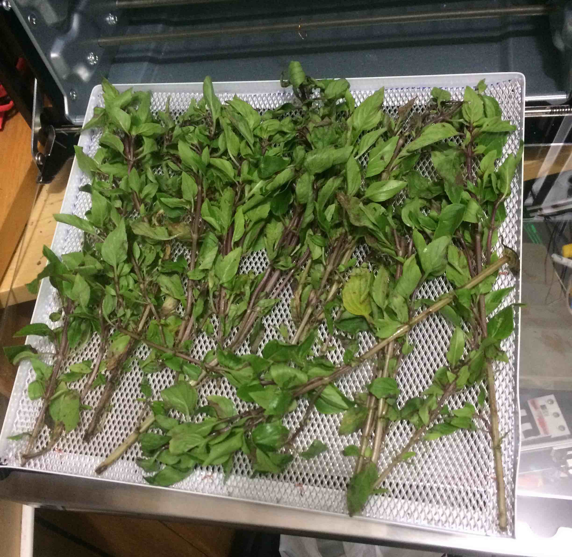
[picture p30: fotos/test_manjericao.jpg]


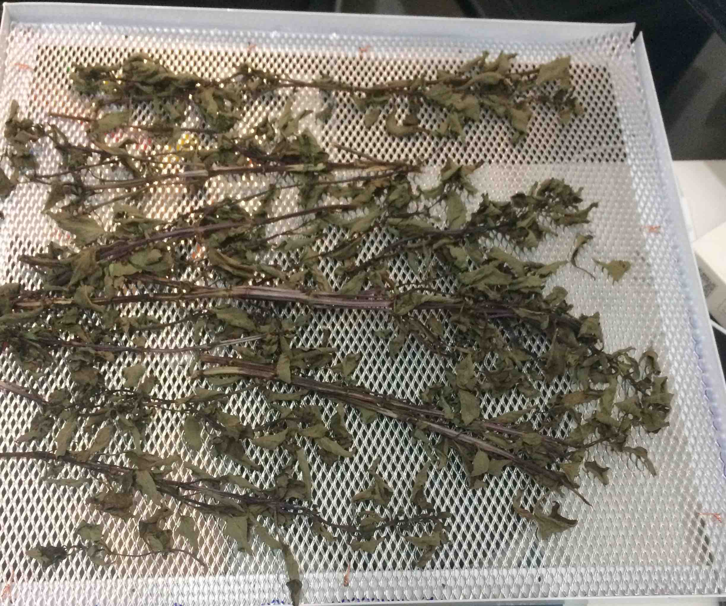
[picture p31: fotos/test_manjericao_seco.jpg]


# 5.1. Teste com banana

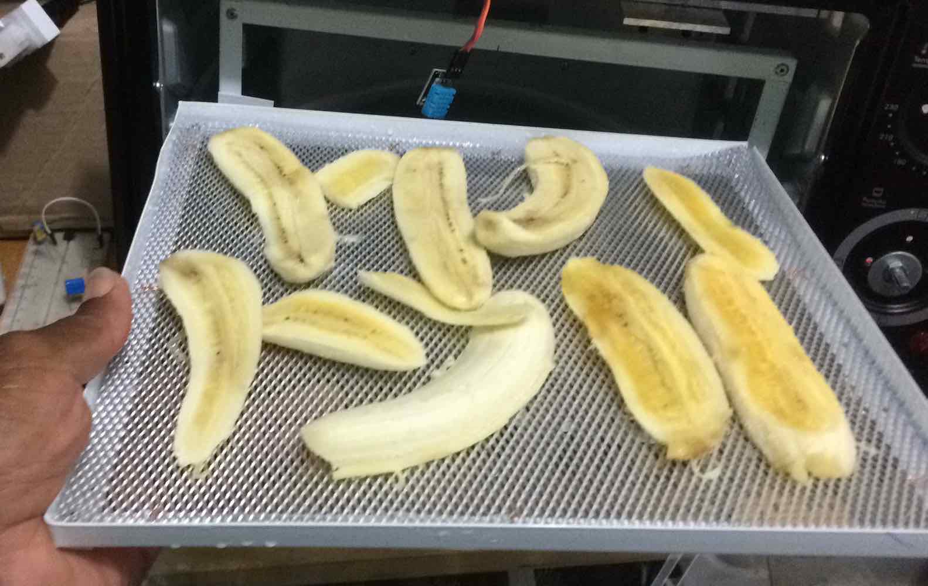
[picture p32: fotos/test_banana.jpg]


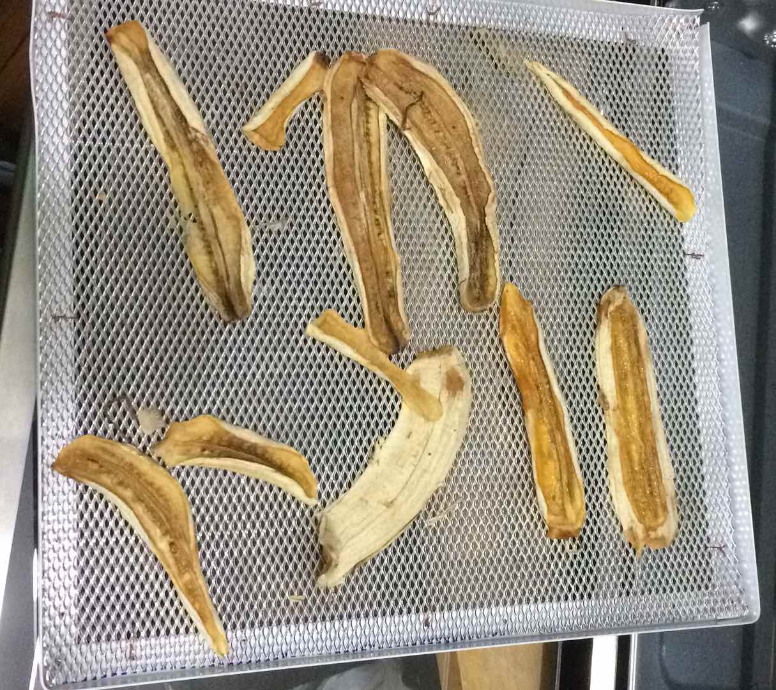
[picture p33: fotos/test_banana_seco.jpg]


Curva de secagem ensaio com banana.

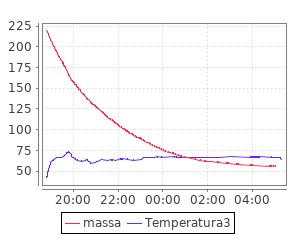
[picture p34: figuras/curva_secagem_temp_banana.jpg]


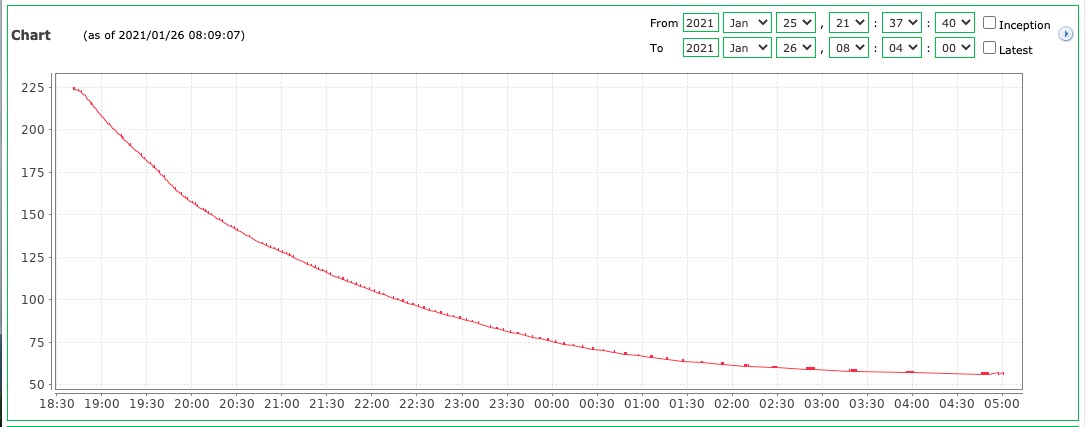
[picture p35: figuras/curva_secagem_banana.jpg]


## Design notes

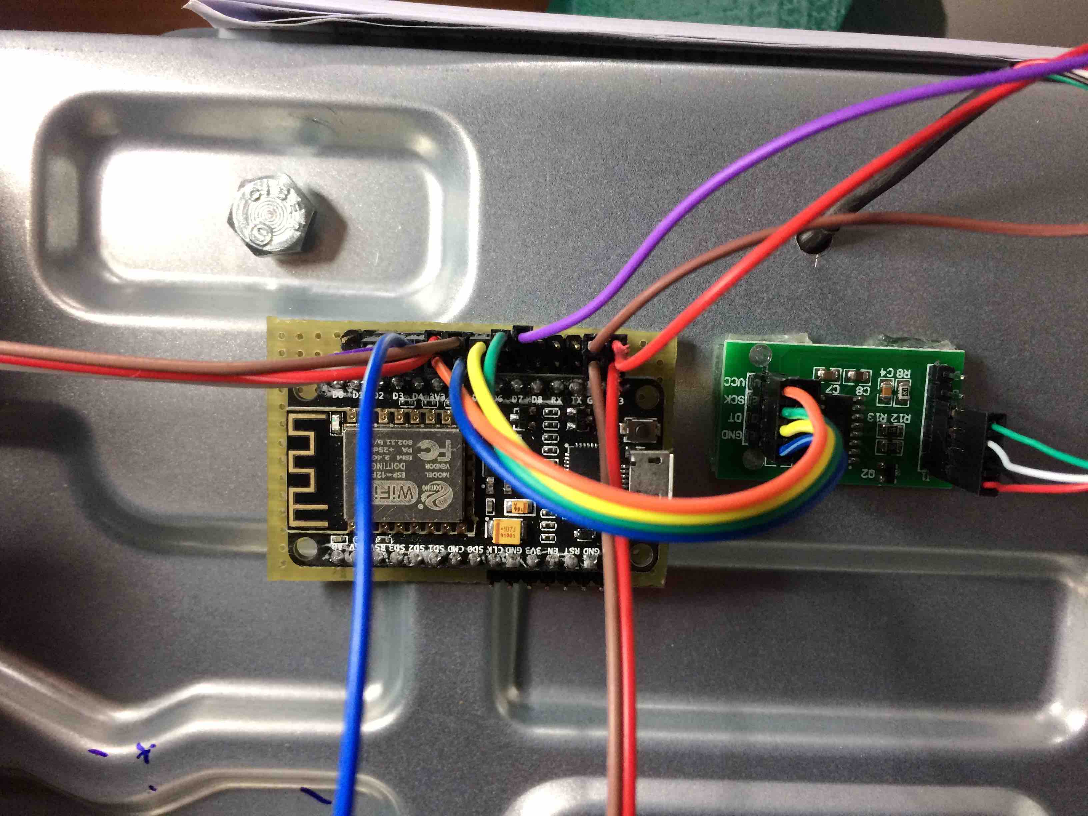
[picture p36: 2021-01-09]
fotos/esp-hx11.jpg

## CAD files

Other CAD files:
sketchup/chamine.skp
sketchup/chamine~.skp

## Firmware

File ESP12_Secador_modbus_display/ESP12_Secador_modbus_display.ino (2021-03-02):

// Desidratador de laboratorio com medição de peso, temperatura e humidade.
// Versao simplificado com ESP webserver 
// 
// 06/12/2020  Primeira Versao com medicao de peso, temperatura testando o ESP12
//             usando HX711, testando com ScadaBR na bancada local 
//             e sensor de temperatura  onewire
// 28/12/2020  segunda versão com celula de carga montado no forno da Britania
//             calibrando com suporte de bandeja em aluminio branco pendurado 
//             nos resistores superiores.
//             Precisa ainda verificar sentido, pois sinal é invertida.
//             Configuracao do IDE Arduino Placa NodeMCU 0.9 (ESP-12 Module)
//             Porta cu.SLAB_USBtoUART
// 29/12/2020  Preparando para usar display TM1637 para depuração e operacao
//             simplificado. OK
// 30/12/2020  Usando o AM2302 Temperatura e humidade como dht2
//             Usando o DH11   Temperatura e humidade como dht1
// 09/01/2021  Versao funcionando com webserver simples
// 12/01/2021  Potenciometro ok, Medicao de velocidade da FAN Ok com interrupcao no pino D7
//             Tem uma instabilidade no DHT22-AM2302 (mais fácil trocar e colocar o DH11).
//             Tentei fazer um controlador proporcional da velocidade da FAN com taxa de amostragem
//             de 1 e 0,5 segundo, mas não funcionou. Vai ter que sintonizar um PID.
//             A interrupcao do Timer não funcionou..  Fiz um soft interrupt no loop 
// 20/01/2021  Soft interrupt usando ticker para medir a frequencia 
//             Re-estruturou o programa separando MODBUS-IP, com mostra de dados pelos serial 
//             Funcionamento também sem Internet pelo serial, 
//             leitura de sensores e escrita pwm no loop principal
//             Falta acertar a fonte e ruidos nos sensores.
// 25/01/2021  Retirada do display, Instalação do sensor DS18B20 no pino D1
//             Resolveu calibraçao do HX711 com set_offset()
//             Resolveu ruído HX711 com resistor pull down de 10K no sinal de Dados
//             Filtro de dados fora do range na temperatura, humidade e massa
//             Versão estável com pouca interferencia de ruidos (Curva de secagem Banana com ScadaBR)
//             Falta 1) trocar DHT11 na saida por um DHT22 pois fica fora da faixa de operacao
//             Falta 2) implementar rotina de controle de velocidade
//             Falta 3) implementar rotina de controle de temperatura
// 31/01/2021  Usando EEPROM para gravar a calibração da balanca eletronica
//             O pino D0 será usada para habilitar a calibracao online 
//             Quando D0 for 0 ele entrará numa rotina de calibracao via serial (ou wifi no futuro)
// 02/02/2021  Implementacao PID com taxa de amastragem de 1 segundo 
//             Parametros PID q0, q1, q2 via ScadaBR base 100
//             Monitoracao Erros e Saida via ScadaBR
//             Habilitacao rotina PID via ScadaBR
//             PID não funcionou muito bem. Vamos ter que encarar outro algoritmo
// 12/02/2021  MODBUS Registradores Saidas
//             0 Temperatura1 
//             1 Humidade1
//             2 Temperatura2 
//             3 Humidade2  
//             4 gramas
//             5 Temperatura3
//             6 velocidade 
//             7 potmeter 
//             8 Erro 
//             9 Saida 
//  
//             MODBUS Registradores Entradas
//             pwm_saida_fan  10
//             pwm_saida_res  11
//             pwm_frequencia 12
//             controle_PI    13
//             q0_PD          14
//             q0             15
//             q1_PD          16
//             q1             17
//             q2_PD          18
//             q2             19
//
// 13/02/2021  Mudando os sensores de temperaturas para trabalhar com décimas de graus.
//             Trabalhando com inteiros multiplicados por 10.
//             Opcao para trabalhar com P, PI, PD e PID selecionado pelo ScadaBR
//
// 22/02/2021  Colocando display OLE e usando TX e RX como IO
//             Impressao de boot OK.. Precisa ainda detalhar WiFi 
//             Impressao de valores no display OK
//             Botao de inicio de secagem OK..
//             Falta ver display na sequencia de calibracao
//             Controle padrao PD com q0=3 e q1=-1 e fan em 600  
//               
//  Hardware
//  A0  potmeter
//  D0  calibracao
//  D1  temperatura one wire
//  D2  PWM_FAN       
//  D3  DHTPIN1 DHT11 (1)   
//  D4  DHTPIN1 DHT11 (2)      
//  D5  DOUT HX711
//  D6  SCK  HX711
//  D7  SENS_ROT
//  D8  PWM_RES
//  TX  OLE_SDA
//  RX  OLE_SCL

// Incluindo display 
//
#include "SSD1306Wire.h"  
// #include "images.h"  
SSD1306Wire display(0x3c, 3, 1);  // (RX=SDA,TX=SCL)

// Temporizadores
// 

#include<Ticker.h>
//Ticker tick_mostra_display;
Ticker tick_temporizador1s;

/* Configurando FAN */
#define PWM_FAN  D2
#define PWM_RES  D8
#define SENS_ROT D7
#define potmeterpin A0

/* Configuracao Wifi e webserver
 *  
 */

#include <ESP8266WiFi.h>
#include "acesso_wifi.h"  // define ssid & password
#include <WiFiClient.h>
#include <ESP8266WebServer.h>
#include <ESP8266mDNS.h>

/* https://circuits4you.com/2018/01/02/esp8266-timer-ticker-example/
#define LED 2
void ICACHE_RAM_ATTR onTimerISR(){
    digitalWrite(LED,!(digitalRead(LED)));  //Toggle LED Pin
    timer1_write(600000);//12us
} */


/* Configuracao Celula de carga 
*/
#include "HX711.h"
const int LOADCELL_DOUT_PIN = D5;
const int LOADCELL_SCK_PIN  = D6;

HX711 scale;
/* calibracao balanca */
#include <EEPROM.h>
#define pin_calibracao D0


/* Temperatura DS18B20*/
/* 
 */
#include <OneWire.h>
#include <DallasTemperature.h>
#define ONE_WIRE_BUS D1 
OneWire oneWire(ONE_WIRE_BUS);
DallasTemperature sensor_ds18(&oneWire);

/* Configuracao sensores DHT11 e DHT22
 *  
 */

//#include <Adafruit_Sensor.h>
#include <DHT.h>
#include <DHT_U.h>
uint32_t delayMS;

#define DHTPIN1 D3  // mudou  
#define DHTTYPE1    DHT11     // DHT 11
DHT_Unified dht1(DHTPIN1, DHTTYPE1);

#define DHTPIN2 D4    // 4  conferir
#define DHTTYPE2    DHT22  // 11     // DHT 22 (AM2302)
// DHT_Unified dht2(DHTPIN2, DHTTYPE2);
DHT dht2(DHTPIN2, DHTTYPE2);

/* Variaveis globais 
 *  
 */
float gramas;
float Temperatura1, Humidade1, Temperatura2, Humidade2;
float Temperatura3; 
int velocidade=0;
volatile byte interruptCounter =0;
int potmeter=0;
unsigned int pwm_frequencia;
int pwm_saida_fan;
int pwm_saida_res;
int segundos=0;


void ICACHE_RAM_ATTR handleInterrupt() {
  interruptCounter++;
}


ESP8266WebServer server(80);

////////////////////////////////////////////
// Configuracao do Modbus

//////// Required for Modbus TCP / IP /// Requerido para Modbus TCP/IP /////////
#define maxInputRegister 20
#define maxHoldingRegister 20
 
#define MB_FC_NONE 0
#define MB_FC_READ_REGISTERS 3 //implemented
#define MB_FC_WRITE_REGISTER 6 //implemented
#define MB_FC_WRITE_MULTIPLE_REGISTERS 16 //implemented
//
// MODBUS Error Codes
//
#define MB_EC_NONE 0
#define MB_EC_ILLEGAL_FUNCTION 1
#define MB_EC_ILLEGAL_DATA_ADDRESS 2
#define MB_EC_ILLEGAL_DATA_VALUE 3
#define MB_EC_SLAVE_DEVICE_FAILURE 4
//
// MODBUS MBAP offsets
//
#define MB_TCP_TID 0
#define MB_TCP_PID 2
#define MB_TCP_LEN 4
#define MB_TCP_UID 6
#define MB_TCP_FUNC 7
#define MB_TCP_REGISTER_START 8
#define MB_TCP_REGISTER_NUMBER 10
 
byte ByteArray[260];
unsigned int MBHoldingRegister[maxHoldingRegister];
 
//////////////////////////////////////////////////////////////////////////

int ModbusTCP_port = 502;
WiFiServer MBServer(ModbusTCP_port);

//////////////////////////////////////////////////////////////////////////

void handleRoot() {
  server.send(200, "text/plain", "Webserver Desidratador esp8266 \n Temperatura 1 = " + String(Temperatura1) + 
    " graus \n Umidade 1     = " + String(Humidade1) + 
  " porcento\n Velocidade    = " + String(velocidade) + 
    " rps   \n Potmeter      = " + String(potmeter) + 
 " unidades \n Peso          = " + String(gramas) + " gramas"  );
}

void handleNotFound() {
  String message = "File Not Found\n\n";
  message += "URI: ";
  message += server.uri();
  message += "\nMethod: ";
  message += (server.method() == HTTP_GET) ? "GET" : "POST";
  message += "\nArguments: ";
  message += server.args();
  message += "\n";
  for (uint8_t i = 0; i < server.args(); i++) {
    message += " " + server.argName(i) + ": " + server.arg(i) + "\n";
  }
  server.send(404, "text/plain", message);
}

unsigned int controle=0;
int Referencia;
float Saida, Saida_1, Erro, Erro_1, Erro_2;
float q0=0.125;
float q1=0.12375;
float q2=0;
unsigned int qPontosDecimais;

void temporizador1s(void)
{
 velocidade=interruptCounter;
 interruptCounter=0;
 segundos++;
 if (controle>0) 
 {
  Saida_1 = Saida;
  Erro_2 = Erro_1;
  Erro_1 = Erro;
  Erro = Referencia - Temperatura2; 
  switch(controle)
  {
   case 1: // Proportional
         Saida = q0 * Erro;
         break;
   case 2: // PI
         Saida = Saida_1 + q0 * Erro;
         break;
   case 3: // PD;
         Saida = q0 * Erro  + q1 * Erro_1;
         break;
   case 4: // PID 
         Saida = Saida_1 + q0 * Erro  + q1 * Erro_1 + q2 * Erro_2;
         break;                      
  }
  if (Saida < 0) { analogWrite(PWM_RES,0); Saida=0; } else
   if (Saida > 1023) { analogWrite(PWM_RES,1023); Saida=1023; } else
    analogWrite(PWM_RES, (unsigned int)Saida);
 }
}

void imprime_serial(void)
{
 display.clear();
 /*Serial.print("Temp1= ");     Serial.print(Temperatura1,1);  
 Serial.print("\t Humid1= "); Serial.print(Humidade1,1); 
 Serial.print("\t Temp2= ");  Serial.print(Temperatura2,1);   
 Serial.print("\t Humid2= "); Serial.print(Humidade2,1); 
 Serial.print("\t Gramas= "); Serial.print(gramas,1); 
 Serial.print("\t Velo= ");   Serial.print(velocidade);
 Serial.print("\t temp3= ");  Serial.print(Temperatura3,1);
 Serial.print("\t pot= ");     Serial.print(potmeter);
 Serial.println(" ");*/
 display.setFont(ArialMT_Plain_10);
 display.drawString( 0, 0, "T1="); display.drawString(20, 0, String(Temperatura1/10,1));   
 display.drawString(50, 0, "H1="); display.drawString(70, 0, String(Humidade1,0));
 display.drawString(85, 0, "H2="); display.drawString(105,0, String(Humidade2,0));
 //T3=
 //Temperatura3/10,1
 //display.drawString( 0,20, "T2="); display.drawString(25,20, String(Temperatura2/10,1)); 
 //display.drawString(60,20, "H2="); display.drawString(85,20, String(Humidade2,0));
 display.setFont(ArialMT_Plain_16);
 display.drawString( 0,17, "Temp="); display.drawString(55,17, String(Temperatura2/10,1));  
 display.drawString( 0,33, "Setp="); display.drawString(55,33, String(potmeter/10));
 display.drawString( 0,49, "Mass="); display.drawString(55,49, String(gramas,1));
 if (controle>0) 
 {
  display.drawString(95,33, "CTR"); 
  display.drawString(105,49, "On");
 } 
 display.display();
}
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

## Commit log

2021-01-09 update de fotos
2021-01-10 Adicionado o circuito de controle
2021-01-13 Atualizacao com controle de FAN
2021-01-13 Atualizando duto de ar
2021-01-26 Update com fonte de alimentacao
2021-02-03 Implementacao da rotina de controle de temperatura (PID)
2021-02-03 Atualizacao controle de temperatura PID
2021-03-02 Atualizando versao com display OLE
    [chamine.skp, chamine~.skp]
